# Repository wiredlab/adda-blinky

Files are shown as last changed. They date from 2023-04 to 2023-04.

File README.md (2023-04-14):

# ADDA Blinky

Demonstration of sampling and quantization concepts.

```mermaid
flowchart LR;
    A(Analog\nInput) --> B(ADC);
    B -->|8b| C(LED 7..0);
    B -->|8b| D(DAC);
    D --> E(Analog\nOutput);
    
    S(Samplerate) --> B;
    S --> D;
```

An analog input signal is applied to an 8-bit resolution analog-to-digital converter (ADC) that is sampling at a known rate.
The output bits are displayed on LEDs.
The data is also immediately applied to a digital-to-analog converter (DAC) at the same sample rate.

All of the features are implemented using an ATtiny1616 and its internal peripherals.

[Schematic](docs/adda-blinky.pdf)

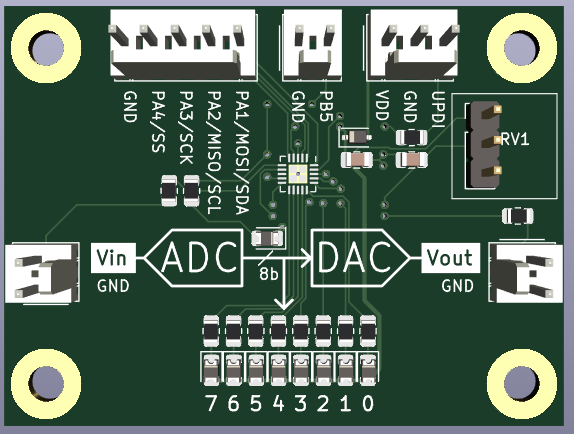
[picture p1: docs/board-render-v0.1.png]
Board render


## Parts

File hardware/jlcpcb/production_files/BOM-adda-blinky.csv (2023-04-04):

Comment | Designator | Footprint | LCSC
220 | R0,R1,R10,R11,R2,R3,R4,R5,R6,R7,R8,R9 | R_0805_2012Metric | C17557
1N5819 | D10 | D_SOD-323 | C191023
1u | C1,C5 | C_0805_2012Metric | C28323
ATtiny1616-M | U2 | VQFN-20-1EP_3x3mm_P0.4mm_EP1.7x1.7mm | C507118
LED | D0,D1,D2,D3,D4,D5,D6,D7,D8 | D_0805_2012Metric | C84256
AOUT | J2 | Molex_KK-254_AE-6410-02A_1x02_P2.54mm_Vertical
AIN | J1 | Molex_KK-254_AE-6410-02A_1x02_P2.54mm_Vertical
PB5 | J3 | Molex_KK-254_AE-6410-02A_1x02_P2.54mm_Vertical
COMM | J4 | Molex_KK-254_AE-6410-05A_1x05_P2.54mm_Vertical
FS | RV1 | PinHeader_1x03_P2.54mm_Vertical
PWR | J5 | Molex_KK-254_AE-6410-03A_1x03_P2.54mm_Vertical

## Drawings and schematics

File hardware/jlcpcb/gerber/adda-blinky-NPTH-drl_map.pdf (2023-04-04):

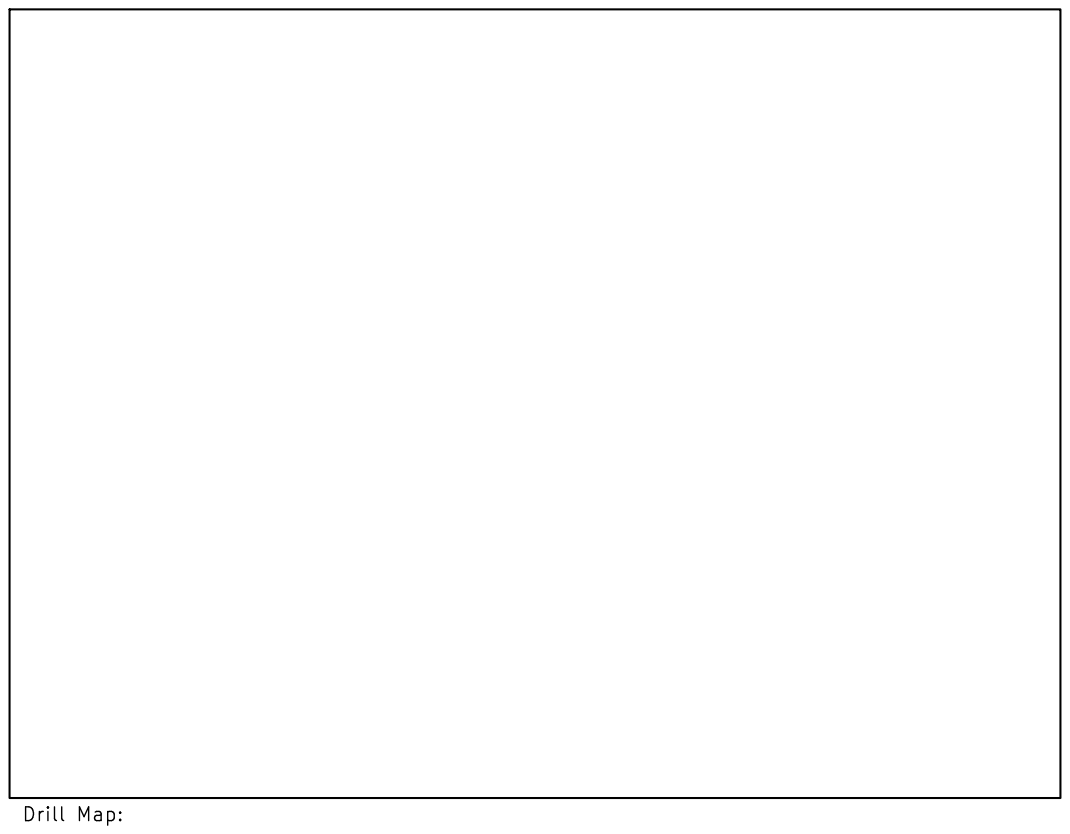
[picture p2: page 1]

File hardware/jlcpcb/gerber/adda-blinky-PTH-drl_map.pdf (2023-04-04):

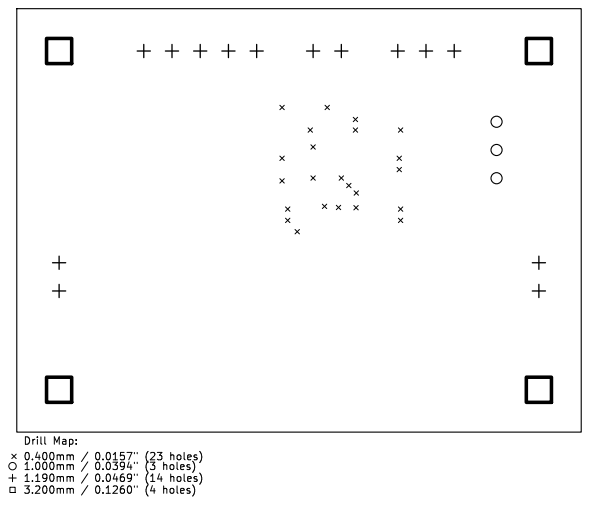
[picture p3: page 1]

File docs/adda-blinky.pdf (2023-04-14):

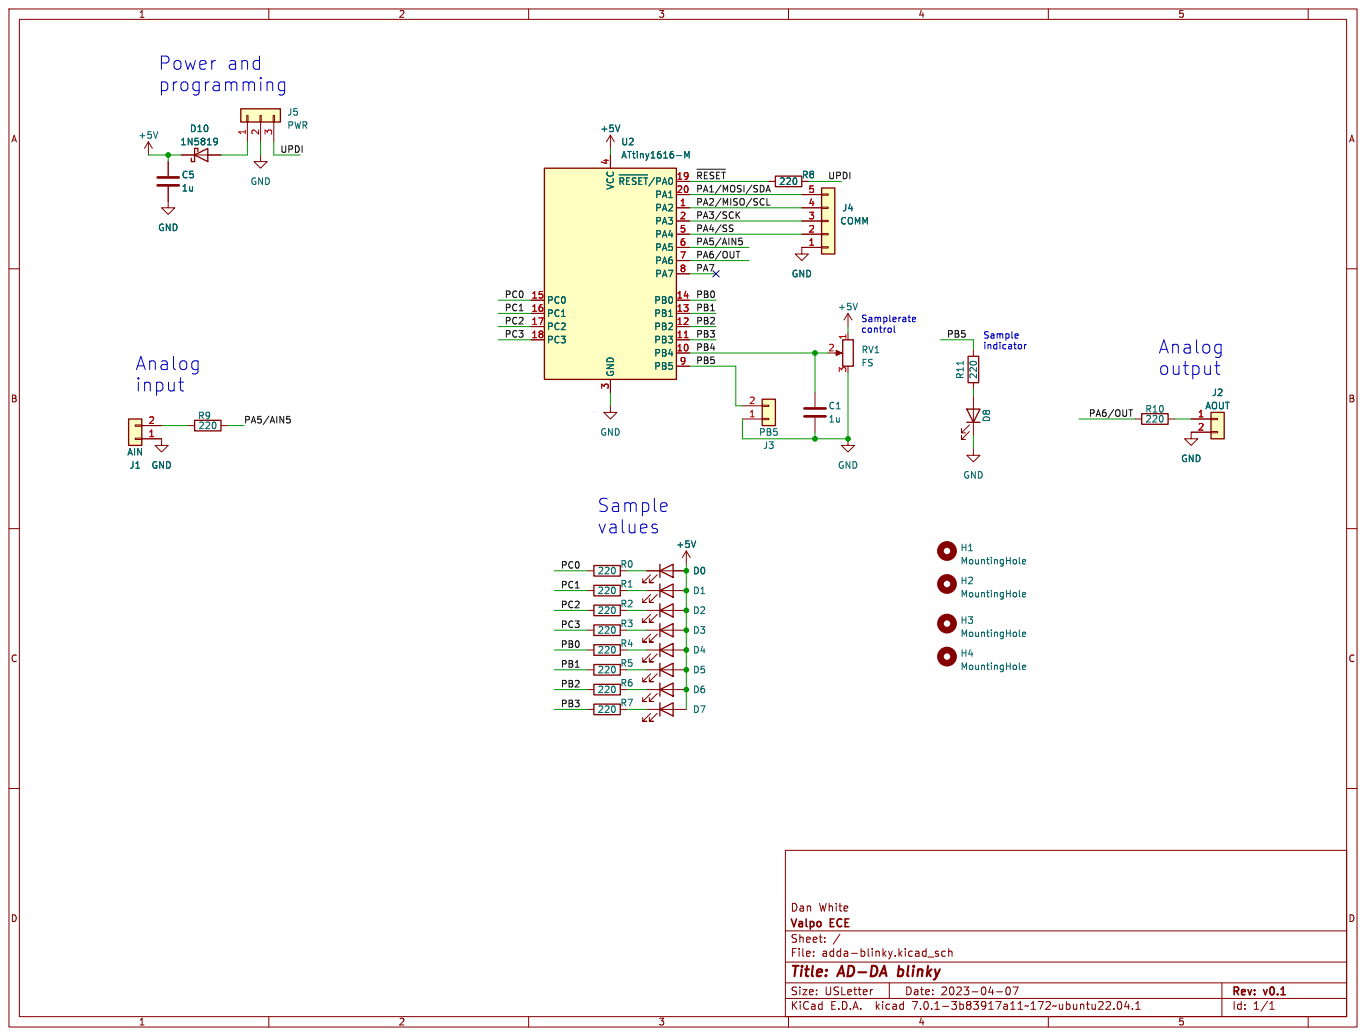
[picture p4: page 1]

Id: 1/1 Title: AD-DA blinky

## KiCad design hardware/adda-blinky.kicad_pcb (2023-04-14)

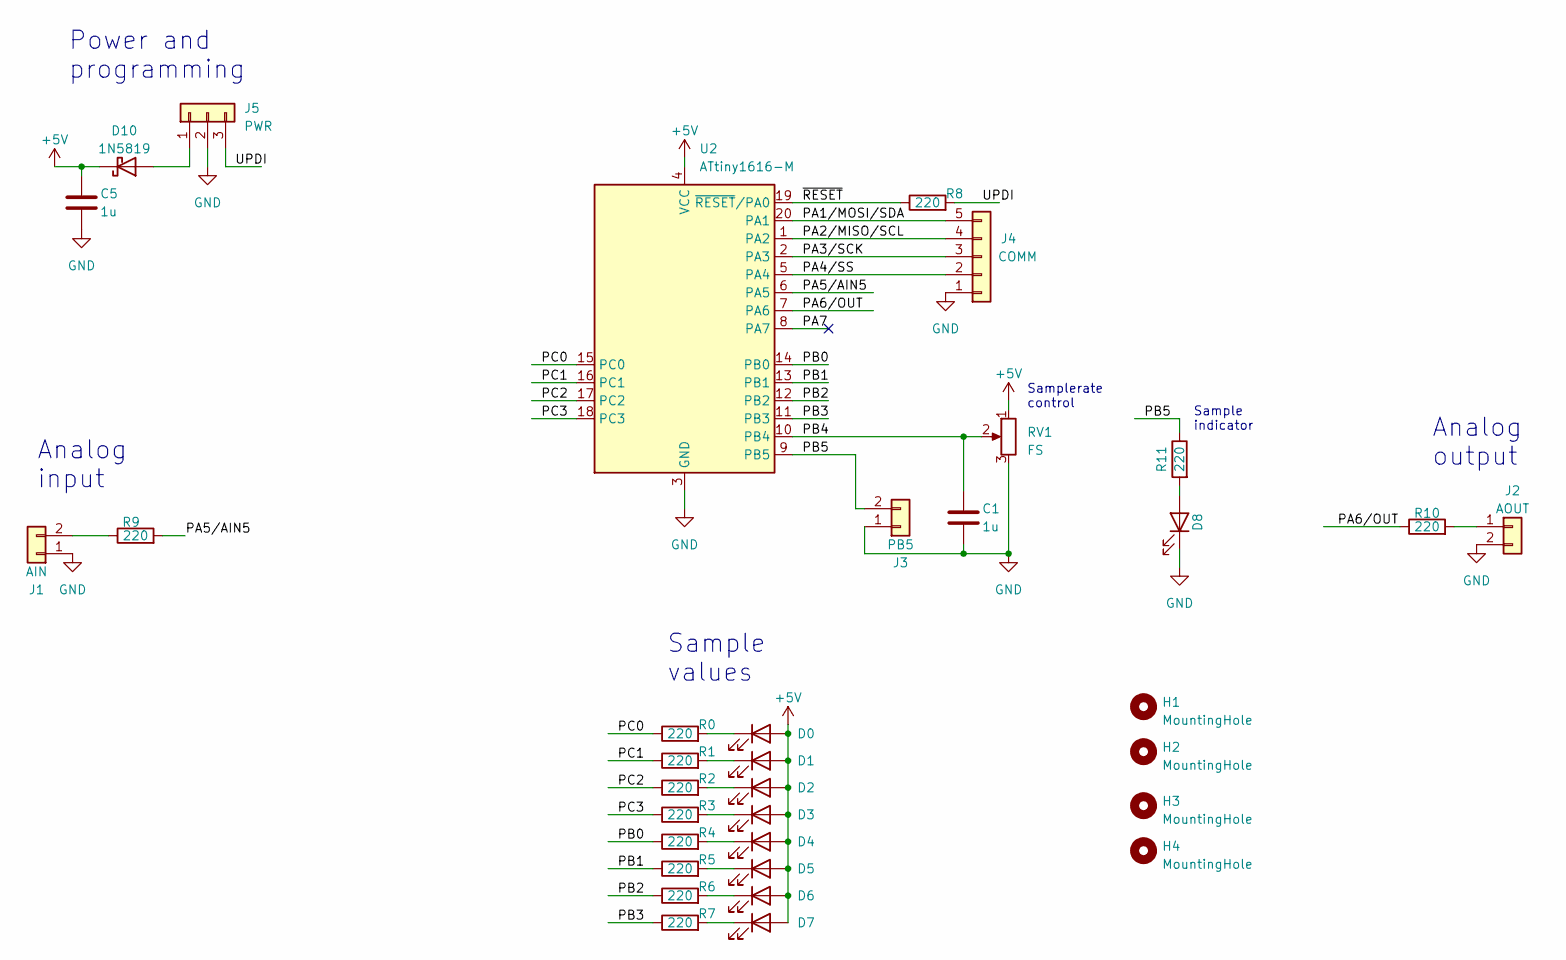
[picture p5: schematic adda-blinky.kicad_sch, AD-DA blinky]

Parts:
C1, C5: 1u; C_0805_2012Metric
D0, D1, D2, D3, D4, D5, D6, D7, D8: LED; D_0805_2012Metric
D10: 1N5819; D_SOD-323
H1, H2, H3, H4: MountingHole; MountingHole_3.2mm_M3_Pad
J1: AIN; Molex_KK-254_AE-6410-02A_1x02_P2.54mm_Vertical
J2: AOUT; Molex_KK-254_AE-6410-02A_1x02_P2.54mm_Vertical
J3: PB5; Molex_KK-254_AE-6410-02A_1x02_P2.54mm_Vertical
J4: COMM; Molex_KK-254_AE-6410-05A_1x05_P2.54mm_Vertical
J5: PWR; Molex_KK-254_AE-6410-03A_1x03_P2.54mm_Vertical
R0, R1, R2, R3, R4, R5, R6, R7, R8, R9, R10, R11: 220; R_0805_2012Metric
RV1: FS; PinHeader_1x03_P2.54mm_Vertical
U2: ATtiny1616-M; VQFN-20-1EP_3x3mm_P0.4mm_EP1.7x1.7mm

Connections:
+5V: C5.1, D0.2 (A), D1.2 (A), D2.2 (A), D3.2 (A), D4.2 (A), D5.2 (A), D6.2 (A), D7.2 (A), D10.1 (K), RV1.1, U2.4 (VCC)
/PA1/MOSI/SDA: J4.5, U2.20 (PA1)
/PA2/MISO/SCL: J4.4, U2.1 (PA2)
/PA3/SCK: J4.3, U2.2 (PA3)
/PA4/SS: J4.2, U2.5 (PA4)
/PA5/AIN5: R9.2, U2.6 (PA5)
/PA6/OUT: R10.1, U2.7 (PA6)
/PA7: U2.8 (PA7)
/PB0: R4.1, U2.14 (PB0)
/PB1: R5.1, U2.13 (PB1)
/PB2: R6.1, U2.12 (PB2)
/PB3: R7.1, U2.11 (PB3)
/PB4: C1.1, RV1.2, U2.10 (PB4)
/PB5: J3.2, R11.1, U2.9 (PB5)
/PC0: R0.1, U2.15 (PC0)
/PC1: R1.1, U2.16 (PC1)
/PC2: R2.1, U2.17 (PC2)
/PC3: R3.1, U2.18 (PC3)
/UPDI: J5.3, R8.2
/~RESET: R8.1, U2.19 (~RESET/PA0)
GND: C1.2, C5.2, D8.1 (K), J1.1, J2.2, J3.1, J4.1, J5.2, RV1.3, U2.3 (GND), U2.21 (GND)
unnamed: D0.1 (K), R0.2
unnamed: D1.1 (K), R1.2
unnamed: D2.1 (K), R2.2
unnamed: D3.1 (K), R3.2
unnamed: D4.1 (K), R4.2
unnamed: D5.1 (K), R5.2
unnamed: D6.1 (K), R6.2
unnamed: D7.1 (K), R7.2
unnamed: D8.2 (A), R11.2
unnamed: D10.2 (A), J5.1
unnamed: J1.2, R9.1
unnamed: J2.1, R10.2

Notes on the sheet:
Sample values
Samplerate control
Power and programming
Sample indicator
Analog output
Analog input

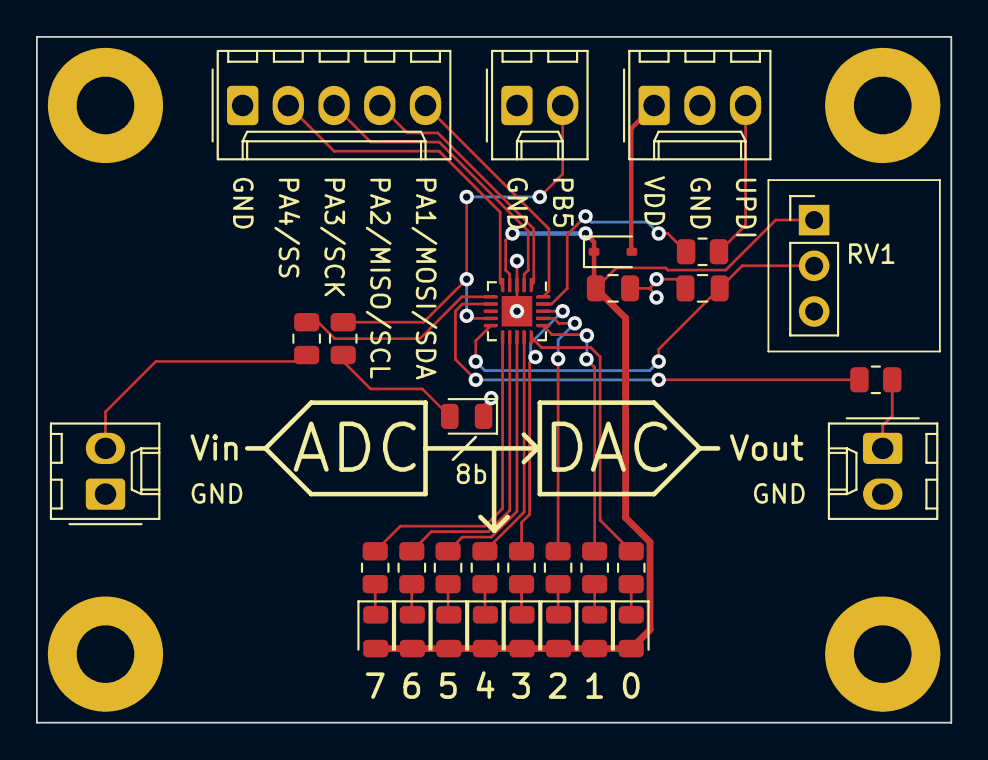
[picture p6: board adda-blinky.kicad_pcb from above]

Board: 2 copper layers, 50.8 x 38.1 mm, 35 parts (0 on the bottom side), 32 nets.

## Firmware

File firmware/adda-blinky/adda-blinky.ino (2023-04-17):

#define ADC_DAC_REFERENCE INTERNAL4V3
#define ANALOG_IN_PIN PIN_PA5
#define ANALOG_OUT_PIN PIN_PA6
#define SAMPLE_PIN PIN_PB5
#define POT_CHECK_INTERVAL_MS 2000
#define POT_PIN PIN_PB4

void setup() {
  // LED output pins
  // PC3..0 --> LED3..0
  PORTC.DIR = (PIN3_bm | PIN2_bm | PIN1_bm | PIN0_bm);

  // PB3..0 --> LED7..4
  PORTB.DIR = (PIN3_bm | PIN2_bm | PIN1_bm | PIN0_bm);

  // PB5 is "Sample indicator" LED
  PORTB.DIRSET = PIN5_bm;


  // Configure the ADC and DAC references
  VREF.CTRLA = (0x03 << 4) | (0x03 << 0);
  VREF.CTRLB = VREF_ADC0REFEN_bm | VREF_DAC0REFEN_bm;

  // ADC setup
  /*
  ADC0.CTRLA = ADC_RESSEL_bm | ADC_FREERUN_bm | ADC_ENABLE_bm;
  ADC0.CTRLC = ADC_SAMPCAP_bm | ADC_PRESC_DIV2_gc;
  ADC0.MUXPOS = ADC_MUXPOS_AIN5_gc;
  ADC0.COMMAND = 1;
  */
  analogReference(INTERNAL4V3);

  // DAC setup
  DAC0.CTRLA = DAC_OUTEN_bm | DAC_ENABLE_bm;


  // Configure timer to set the sample rate
  // clock divider
  TCA0.SINGLE.CTRLA = TCA_SINGLE_CLKSEL_DIV1024_gc | TCA_SINGLE_ENABLE_bm;
  TCA0.SINGLE.CTRLB = TCA_SINGLE_WGMODE_NORMAL_gc;
  TCA0.SINGLE.INTCTRL = TCA_SINGLE_OVF_bm;

  // periodic interrupt
  TCA0.SINGLE.CMP0 = 1000;
  TCA0.SINGLE.PER = 1000;

  sei();
}


void set_data_leds(int16_t data8b) {
  PORTC.OUT = (0xF0 & PORTC.OUT) | (0x0F & ~data8b);
  PORTB.OUT = (0xF0 & PORTB.OUT) | (0x0F & (~data8b >> 4));
}



void set_sample_rate(int16_t val) {
  if (val < 0x20) {
    // 1 Hz
  }
  else if (val < 0x40) {
    // 10 Hz
  }
  else if (val < 0x60) {
    // 100 Hz
  }
  else if (val < 0x80) {
    // 1 kHz
  }
  else if (val < 0xA0) {
    // 3 kHz
  }
  else if (val < 0xC0) {
    // 10 kHz
  }
  else if (val < 0xE0) {
    // 20 kHz
  }
  else {
    // max
  }
}

ISR(TCA0_OVF_vect) {
  int16_t signal_val;
  int16_t adc_raw;

  // Sample indicator
  digitalWrite(SAMPLE_PIN, 1);
  
  // sample
  
  //signal_val = 0xFF & millis()>>5;
  adc_raw = analogRead(ANALOG_IN_PIN);
  signal_val = adc_raw >> 2;

  //signal_val = analogRead(POT_PIN) >> 2;
  //signal_val = ADC0.RESL;
  
  // display
  set_data_leds(signal_val);

  // output
  //analogWrite(ANALOG_OUT_PIN, signal_val);
  DAC0.DATA = signal_val;


  // AVR 1-series needs to clear the interrupt flag
  TCA0.SINGLE.INTFLAGS = TCA_SINGLE_OVF_bm;
  ADC0.COMMAND = 1;

  // Sample indicator
  digitalWrite(SAMPLE_PIN, 0);
}



void loop() {
  unsigned long last_check = 0;
  unsigned long now;
  int16_t potval;

  now = millis();

  if ((now - last_check) > POT_CHECK_INTERVAL_MS) {
    cli();
    potval = analogRead(POT_PIN) >> 2;
    sei();
    set_sample_rate(potval);
    //set_data_leds(potval);

    //digitalWrite(PIN_PC0, ADC0.COMMAND);
    TCA0.SINGLE.PER = 20000;
    last_check = now;
  }
}

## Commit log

2023-04-02 WIP add bus LEDs
    [adda-blinky.kicad_pcb, adda-blinky.kicad_sch]
2023-04-02 Rename hardware subdir
    [adda-blinky.kicad_pcb, adda-blinky.kicad_sch]
2023-04-03 First order
    [adda-blinky.kicad_pcb, adda-blinky.kicad_sch]
2023-04-03 add fab outputs
    [BOM-adda-blinky.csv, CPL-adda-blinky.csv, adda-blinky-CuBottom.gbr, adda-blinky-CuTop.gbr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]
2023-04-03 Add series resistors to I/Os
    [BOM-adda-blinky.csv, CPL-adda-blinky.csv, adda-blinky-CuBottom.gbr, adda-blinky-CuTop.gbr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]
2023-04-03 Fixup MCU rotation
    [CPL-adda-blinky.csv, adda-blinky-CuBottom.gbr, adda-blinky-CuTop.gbr, adda-blinky-EdgeCuts.gbr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]
2023-04-03 Add LED to PB5 for status and sample indicator
    [BOM-adda-blinky.csv, CPL-adda-blinky.csv, adda-blinky-CuBottom.gbr, adda-blinky-CuTop.gbr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]
2023-04-04 Swap LED orientation
    [BOM-adda-blinky.csv, CPL-adda-blinky.csv, adda-blinky-CuBottom.gbr, adda-blinky-CuTop.gbr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]
2023-04-14 Add board render and update title blocks
    [adda-blinky.kicad_pcb, adda-blinky.kicad_sch]
